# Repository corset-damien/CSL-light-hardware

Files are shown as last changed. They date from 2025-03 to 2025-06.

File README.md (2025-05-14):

# CSL-light-hardware

## I. Objectives 
### LED module operating modes with a pcb plate

#### MODE 1 - Sequence of pulses
The user can define on the computer the frequency and amplitude of a sequence of pulses.

#### MODE 2 - Analog control 
The user can send an analog signal to control the LED. The analog signal can be designed using eg. a signal generator. 

#### MODE 3 - Manual control
The user can set the LED level using a potentiometer.

## II. Usage

### I. Access mode 
- **To access Mode 1**: set interruptor to 1 ("serial" shows up on the screen) and switch the flip to PWM.
- **To access Mode 2**: set interruptor to 1 ("serial" shows up on the screen) and switch the flip to analog.
- **To access Mode 3**: set interruptor to 0 ("manual" shows up on the screen).

### II. Connection 
- Insert the LED jacks into the corresponding holes
- Insert the generator jacks into the corresponding holes
- Insert the jacks to feed the analog signals into the corresponding input holes

<p align="center">
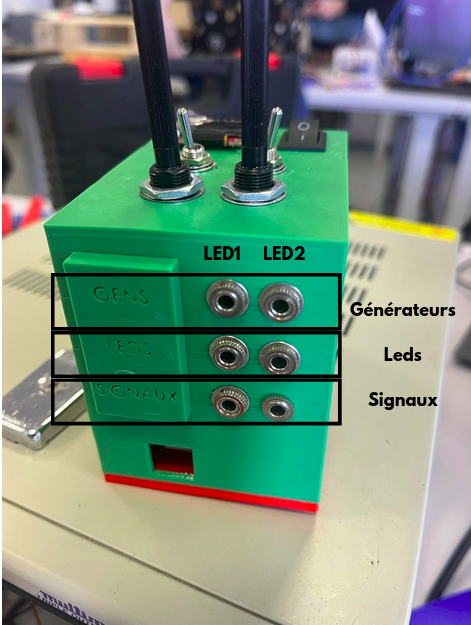
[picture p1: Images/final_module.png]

</p>

### III. Using the LEDControl_interrupt_screen_ascii code

First, open the LEDControl_interrupt_screen_ascii.cpp code in Arduino.ide.
To run the program, you must first have the SSD1306Ascii library installed on Arduino.

[Explains how to control light sources with Arduino and Python, and generate a trigger signal to synchronize a camera](https://github.com/SonyCSLParis/CSL-Lights)

Test the control command: 
- type: #d[3,0,0,1,0,2,0,255]:xxxx.  
  It is a command to generate on and off output on pin 3 or 6.
  The pin stays on for 1 seconds with a period of 2 seconds, at intensity 255. 
  It is later on embeded in a Pyton code for clarity. 
  You should see a character sequence appear. 
- Then type #b[100,0]:xxxx to start the experiment. 
  You should see the LEDs blink (frequency 0.5Hz). 
- To stop the blinking, type #e:xxxx

## III. Manufacture

### I. Kicad

[Kicad Folder](https://github.com/Julie-Mauguit/CSL-light-hardware/tree/main/Kicad%20pcb)

#### A. Complete electronic circuit

Complete Circuit on Kicad : 

<p align="center">
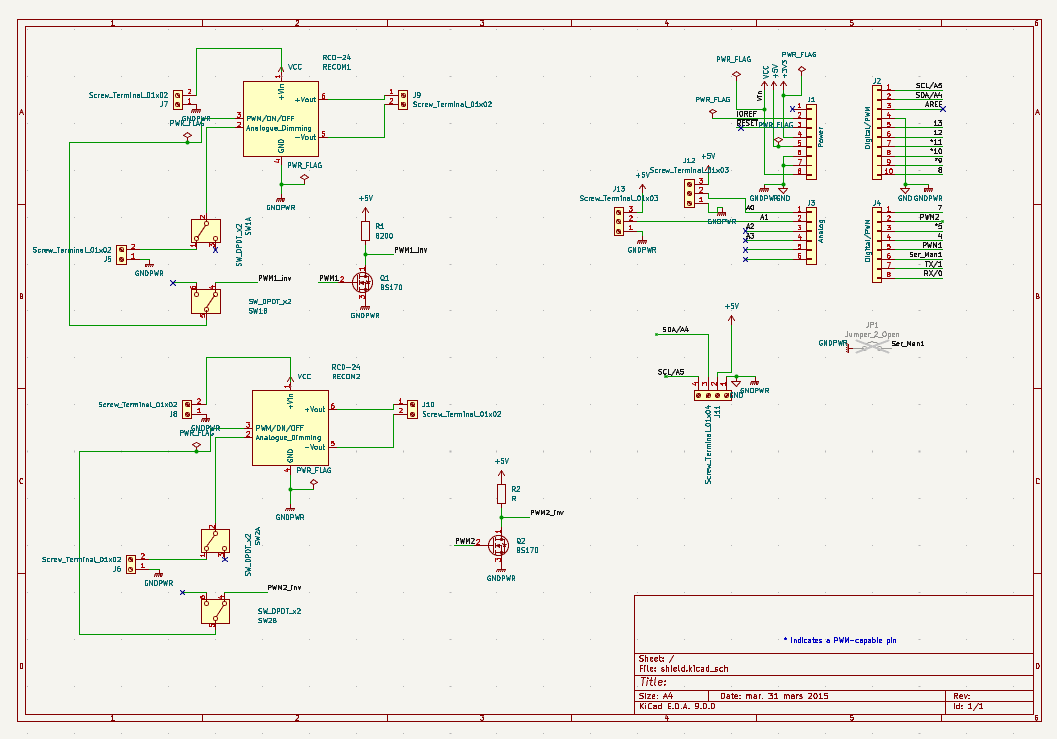
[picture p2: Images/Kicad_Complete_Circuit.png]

</p>

LED 1 and 2 : 

<p align="center">
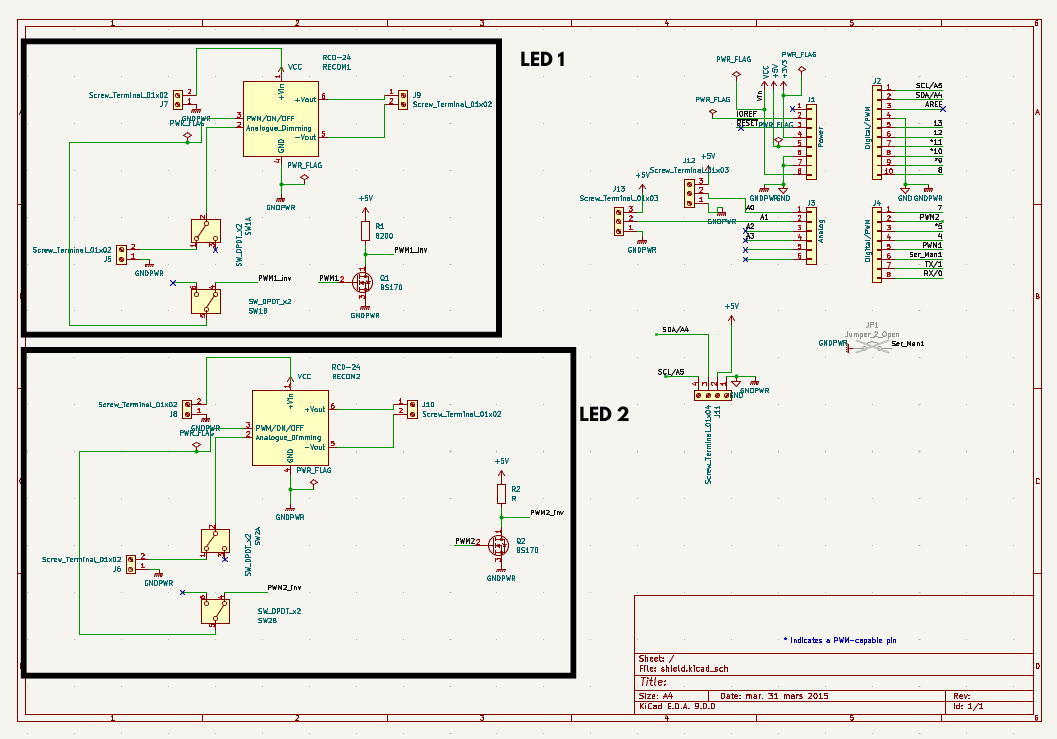
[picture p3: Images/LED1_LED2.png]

</p>

PWM Control : 

<p align="center">
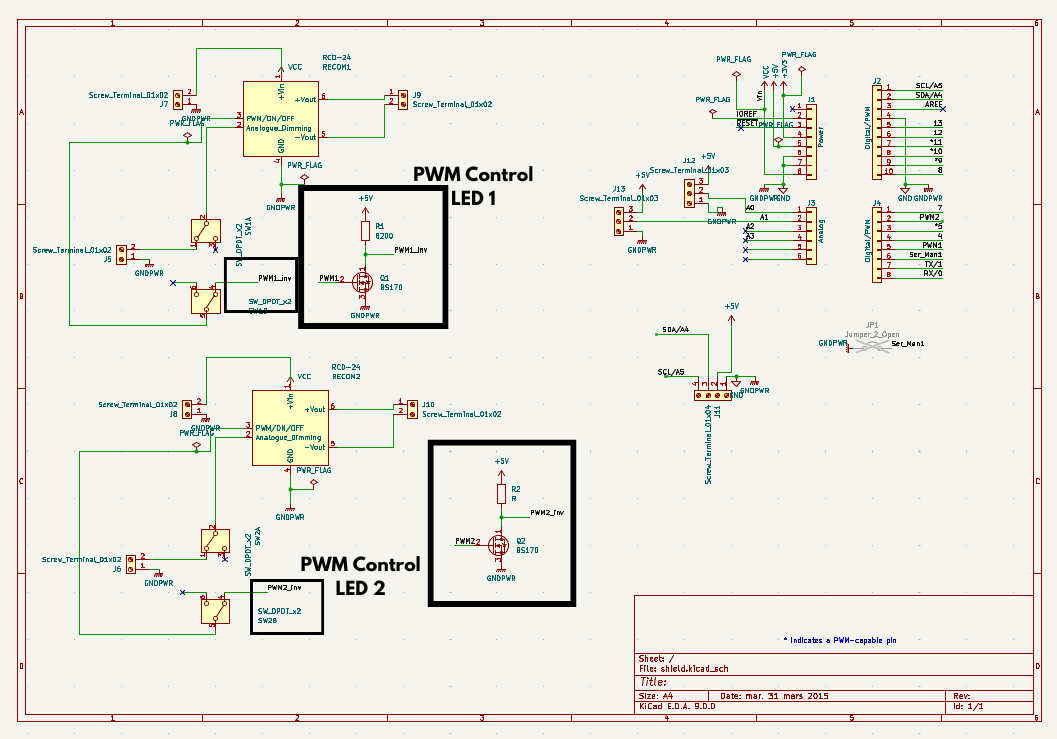
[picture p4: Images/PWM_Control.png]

</p>

Analog Control : 

<p align="center">
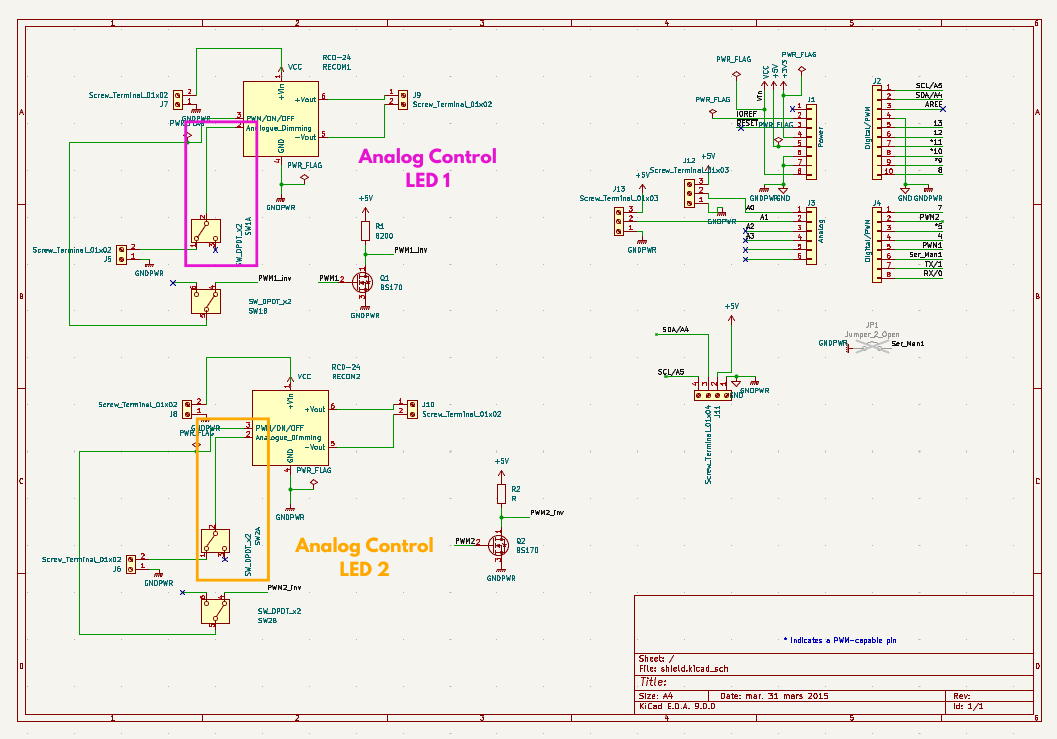
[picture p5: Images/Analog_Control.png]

</p>

Serial or Manual Mode : 

<p align="center">
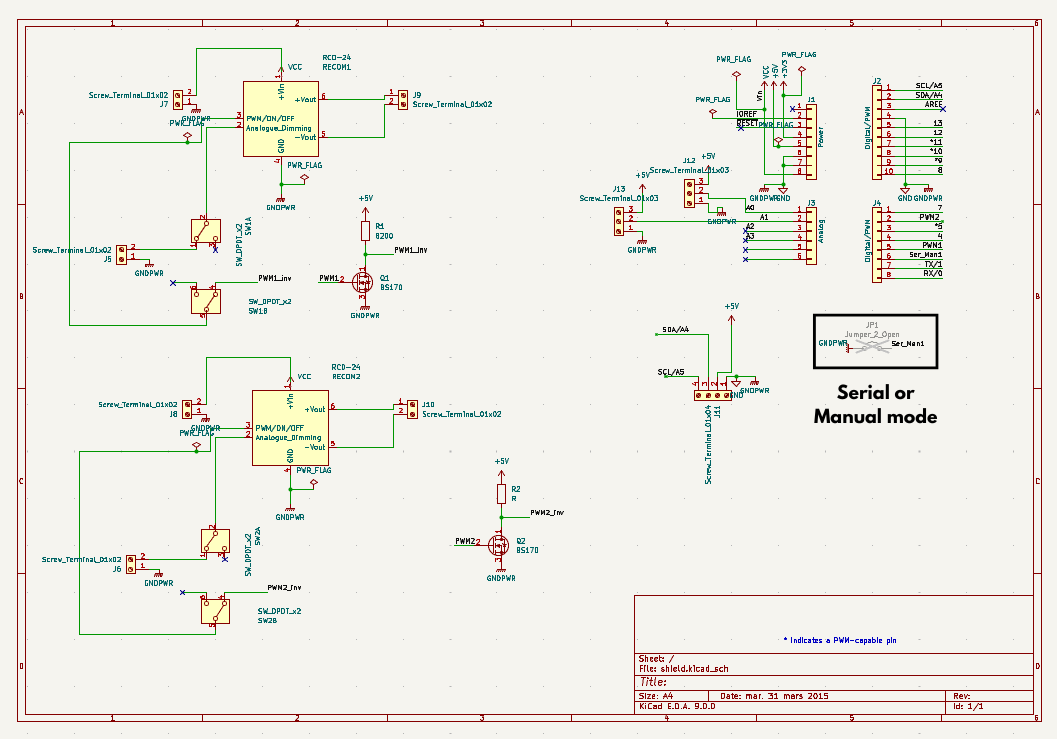
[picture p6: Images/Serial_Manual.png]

</p>

#### B. Component roles
- **Top connectors (J5, J7, J6, J8, J10)** :
  These are screw terminal blocks used to connect LEDs, power, or other peripherals.
- **Relays (RECOM1, RECOM2, etc.)** :
Their role is to adjust the LED light output to prevent damage. They therefore act as power regulators.
- **MOSFETs (BS170)** :
These are used to invert the signal. In fact, the RECOM inverts the input signal, it is inverted a first time before it processes it, in order to obtain the initially desired signal at the output. This can be useful if the LEDs require active low control (they light up when the signal is LOW).
- **Potentiometers (RV1, RV2)** :
These allow for a manual mode to adjust LED intensity via an analog input.
- **Double Switch (SW_DPDT_x2)** :
Two switches are used to select between analog or PWM control for each LED.
- **A Switch On-Off (Jumper_2_Open)** :
It allows switching between Serial and Manual modes.

#### C. Impression

It lasts about 30 minutes.

<p align="center">
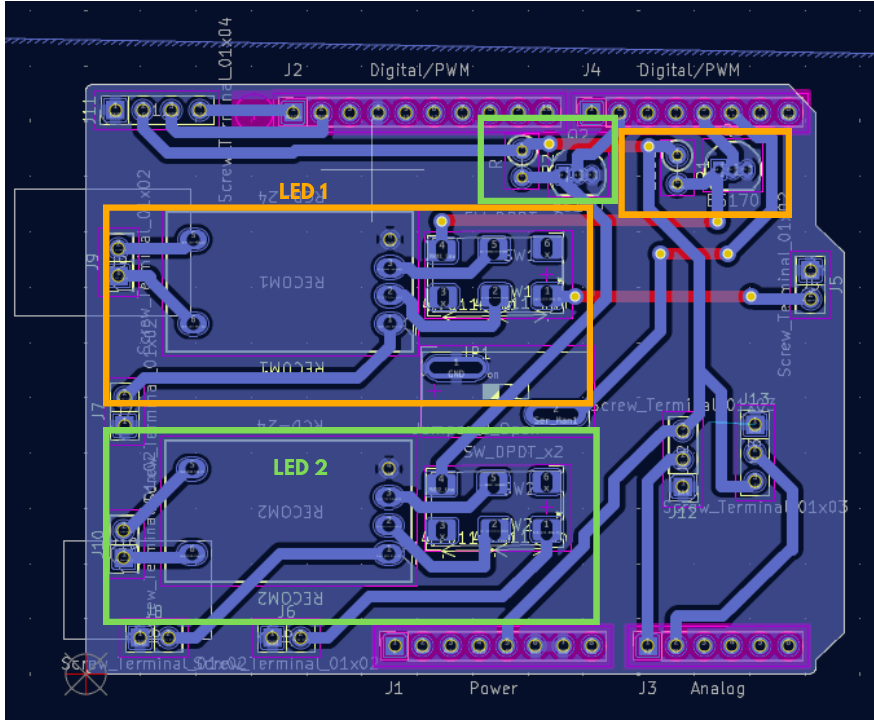
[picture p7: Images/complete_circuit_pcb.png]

</p>

### II. Welding

#### A. Shield Arduino
First, you need to solder the branches of the Arduino.

#### B. Components that you solder directly onto the PCB board
- Resistors
- MOSFET transistors
- RECOM
- Terminal blocks
- Vias

#### C. Components that you don't solder directly onto the PCB board
- The 2 potentiometers
- The OLED screen
- The 2 switches
- The on-off switch

<p align="center">
  <strong>After welding</strong><br>
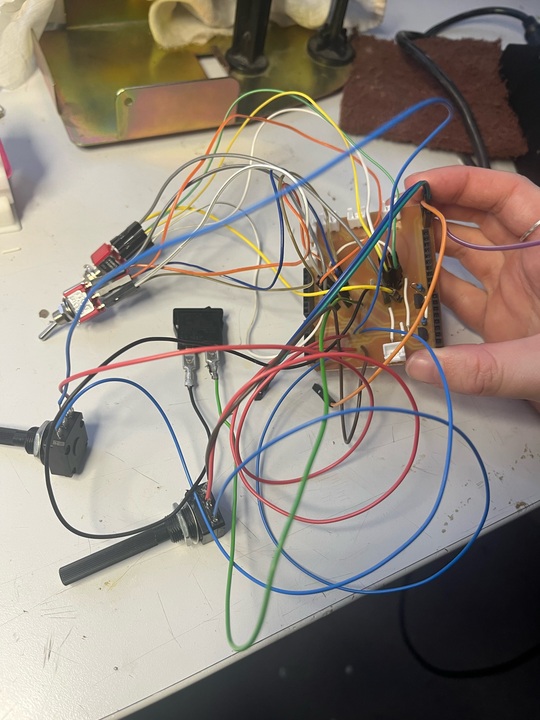
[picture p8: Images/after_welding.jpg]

</p>

#### D. Jack sockets
You have to solder cables with the female jack sockets.

<p align="center">
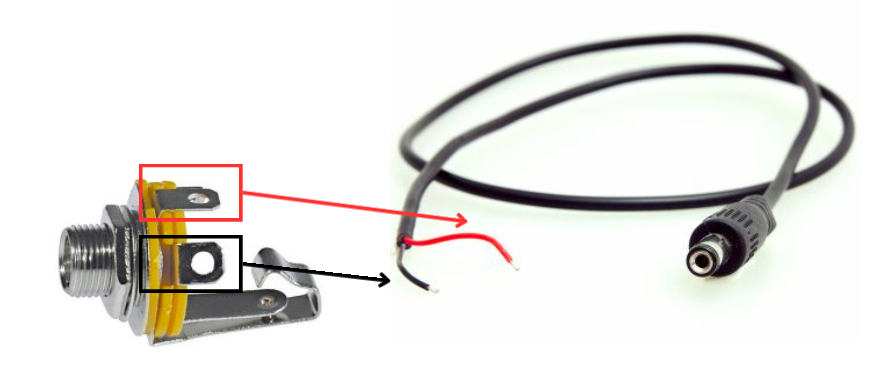
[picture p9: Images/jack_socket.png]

</p>

For the black and red cables of the male jack, you must solder them to the generator, LED, and signal cables.
Before soldering, prepare some heat-shrink tubing to prevent loose connections.

#### E. List of components

On GOTRRONIC : 

- **RECOM** : (x2)
  - Web link: https://www.gotronic.fr/art-convertisseur-r-78e3-3-0-5-29589.htm
  - Code : 14977
  - Price : 4,6€

- **Switch On-Off**: (x1)
  - Web link : https://www.gotronic.fr/art-inter-secteur-unipolaire-47432.htm
  - Code : 07059
  - Price : 0.90€

- **OLED Screen** : (x1)
  - Web link : https://www.gotronic.fr/art-module-afficheur-oled-0-96-tf052-28511.htm
  - Code : 36038
  - Price : 9,5€

- **Potentiometers** : (x2)
  - Web link : https://www.gotronic.fr/art-potentiometre-logarithmique-10k-937-3000.htm
  - Code : 04519
  - Price : 2,60€

 - **Double switch** : (x2)
    - Web link : https://www.gotronic.fr/art-inverseur-bipolaire-8012b-4181.htm
    - Code : 07014
    - Price : 2,80€
      
- **Resistors 820 ohms** : (x2)
    - Web link : https://www.gotronic.fr/art-resistance-carbone-1w-820-8486-2748.htm
    - Code :  04235
    - Price : 0,10€
      
- **2.5mm pitch terminal block** : (x6)
    - Web link : https://www.gotronic.fr/art-bornier-sc02-2-54-15468.htm
    - Code : 48930
    - Price : 0.80€
      
 - **3.5 mm male jack** : (x6)
    - Web link : https://www.gotronic.fr/art-cordon-jack-vers-fils-denudes-sterf-37803.htm
    - Code : 48239
    - Price : 0,95€
  
 - **3.5mm female socket** : (x6)
     - Web link : https://www.gotronic.fr/art-embase-femelle-cg203-4814.htm
     - Code : 08461
     - Price : 0,50€

 - **Transistor MOSFET BS170** : (x2)
     - Web link : https://www.gotronic.fr/art-transistor-bs170-1569.htm
     - Code : 02440
     - Price : 0.30€

- **Uno Arduino** : (x1)
    - Web link : https://www.gotronic.fr/art-arduino-uno-a000066-12420.htm
    - Code : 25950
    - Price : 23.90€

- **9-pin Arduino connector** : (x3)
    - Web link : https://www.gotronic.fr/art-connecteur-fh1x9-35491.htm
    - Code : 49007
    - Price : 0.80€
      
- **14-pin Arduino connector** : (x1)
    - Web link : https://www.gotronic.fr/art-connecteur-fh1x14-35646.htm
    - Code : 49011
    - Price : 1€
      
- **LED** : (x2)
    - Web link: https://www.gotronic.fr/art-led-5-mm-led5bt-21009.htm
    - Code :  03039
    - Price : 0.30€

### III. Assembly

#### A. Box printing

[Solidworks box](https://github.com/Julie-Mauguit/CSL-light-hardware/tree/main/Solidworks%20bo%C3%AEte)

Printing the box takes approximately 1 hour and 20 minutes.
Printing the box lid takes approximately 30 minutes.
Printing the small panel with the instructions takes approximately 13 minutes.

#### B. Plastic inserts

You will need to make three 3.7mm diameter, 3mm deep plastic inserts with 6mm long M3 screws to secure the Arduino to the enclosure lid. 
Then, make 3mm diameter, 3mm deep plastic inserts with 8mm long M3 screws to close the enclosure.

#### C. Finalization

Screw the components into the box in this order:
- Female jack sockets
- OLED display with 10mm long M2 screws and nuts
- The two switches
- The on-off switch
- The two potentiometers

<p align="center">
  <strong>After assembly</strong><br>
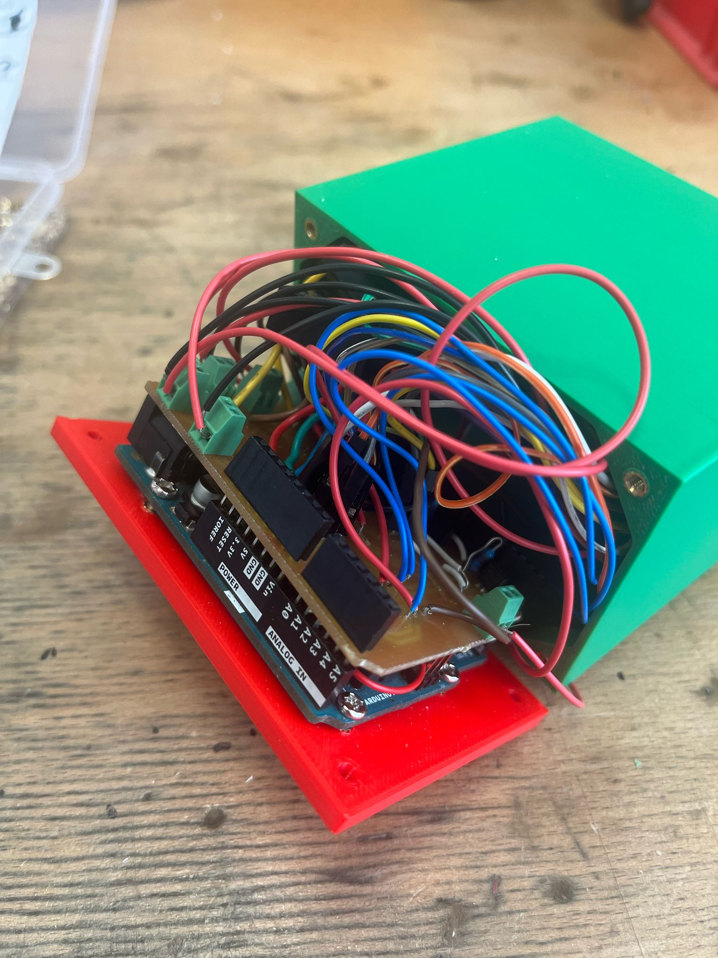
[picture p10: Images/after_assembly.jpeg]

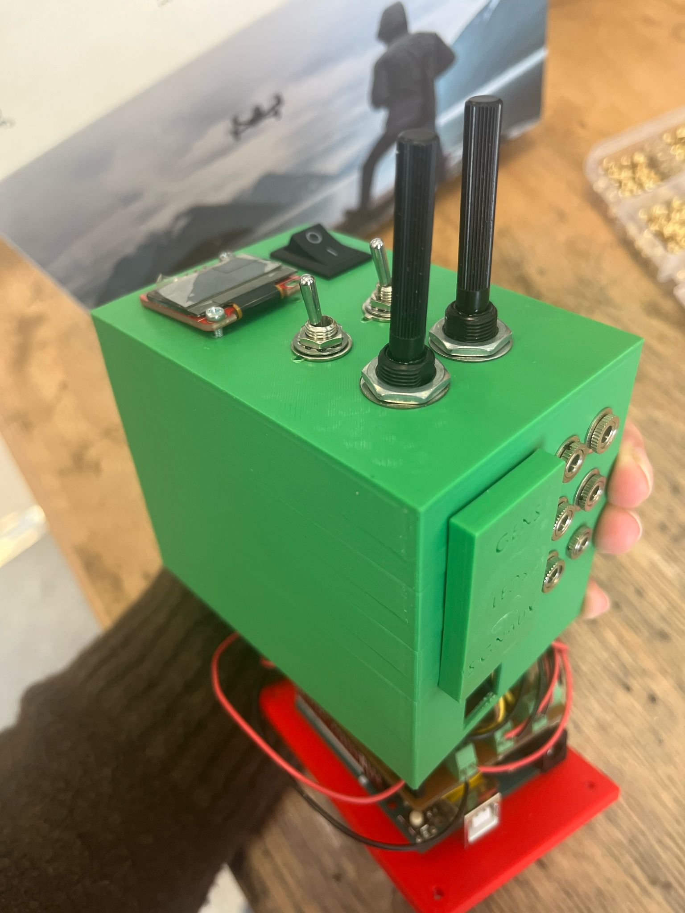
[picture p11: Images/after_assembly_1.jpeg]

</p>

### IV. Code

[Code Arduino/LEDControl_interrupt_screen_ascii](https://github.com/Julie-Mauguit/CSL-light-hardware/tree/main/Code%20Arduino/LEDControl_interrupt_screen_ascii)

The code has been adapted to suit the circuit. 
In this configuration, pins 3 and 6 are used for PWM inputs, while pins A0 and A1 are used for analog inputs.

[Explains how to control light sources with Arduino and Python, and generate a trigger signal to synchronize a camera](https://github.com/SonyCSLParis/CSL-Lights)

### License

Copyright (C) 2025 

Author(s):
Julie Maugit - Polytech Sorbonne
Thierry Legou - CNRS/Aix-Marseille Université
Peter Hanappe - Sony Computer Science Laboratories Paris
Aliénor Lahlou - Sony Computer Science Laboratories Paris

You can redistribute it and/or modify  it under the terms of the GNU General Public License as published by   the Free Software Foundation, either version 3 of the License, or   (at your option) any later version.  This project is distributed in the hope that it will be useful, but  WITHOUT ANY WARRANTY; without even the implied warranty of   MERCHANTABILITY or FITNESS FOR A PARTICULAR PURPOSE.  See the GNU  General Public License for more details.  You should have received a copy of the GNU General Public License  along with this program.  If not, see  <http://www.gnu.org/licenses/>.

This work was supported by the European Innovation Council Pathfinder Open DREAM (grant no. 101046451)

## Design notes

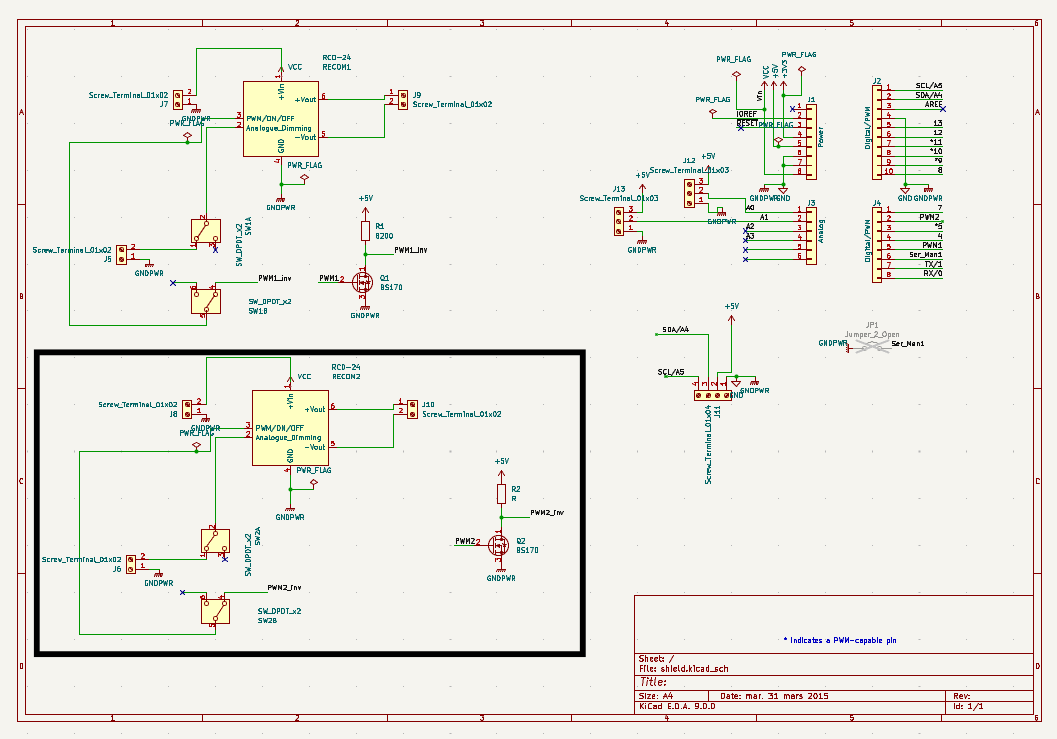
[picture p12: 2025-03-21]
Images/LED 2.png

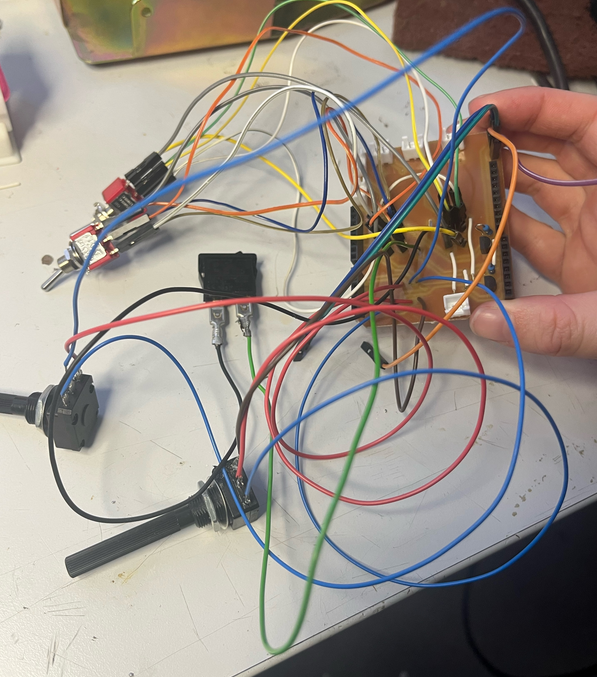
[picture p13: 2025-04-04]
Images/pcb_plate.png

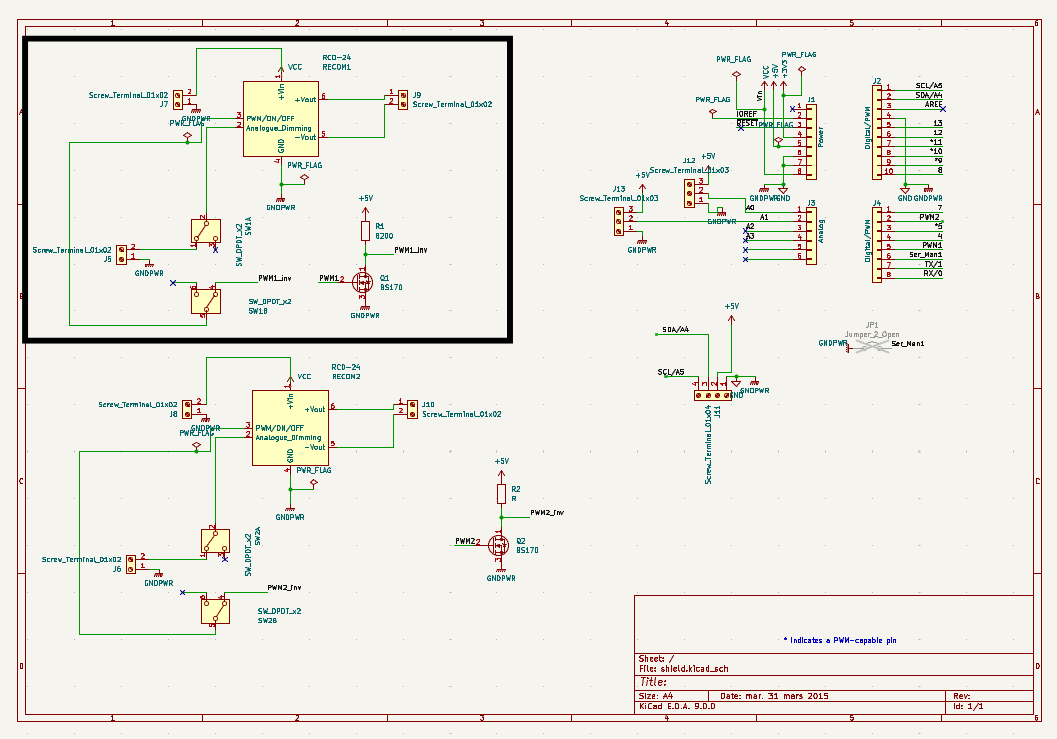
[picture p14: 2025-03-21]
Images/LED 1.png

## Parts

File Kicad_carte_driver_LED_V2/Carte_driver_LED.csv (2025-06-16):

Source: | C:\Users\damie\OneDrive\Bureau\Stage_Sony_CSL_CORSET_Damien\Projets_principaux\led_controler\Kicad\Carte_driver_LED\Carte_driver_LED.kicad_sch
Date: | 28/04/2025 18:29:50
Tool: | Eeschema 7.0.10
Generator: | C:\Program Files\KiCad\7.0\bin\scripting\plugins/bom_csv_grouped_by_value.py
Component Count: | 41
Collated Components:
Item | Qty | Reference(s) | Value | LibPart | Footprint | Datasheet | DNP | Availability | Check_prices | Description | MANUFACTURER | MF | MP | PARTREV | Package | Price | STANDARD | SnapEDA_Link
1 | 2 | C1, C2 | 2.2u | Device:C | Capacitor_SMD:CP_Elec_5x5.3 | ~
2 | 2 | C3, C4 | 10n | Device:C | Capacitor_SMD:C_1206_3216Metric_Pad1.33x1.80mm_HandSolder | ~
3 | 4 | C5, C6, C9, C10 | 2.2n | Device:C | Capacitor_SMD:C_1206_3216Metric_Pad1.33x1.80mm_HandSolder | ~
4 | 8 | C7, C8, C11, C12, C13, C14, C15, C16 | 100n | Device:C | Capacitor_SMD:C_1206_3216Metric_Pad1.33x1.80mm_HandSolder | ~
5 | 2 | C17, C20 | 10u | Device:C | Capacitor_SMD:CP_Elec_5x5.3 | ~
6 | 1 | C18 | 100n | Device:C | Capacitor_Tantalum_SMD:CP_EIA-1608-08_AVX-J_Pad1.25x1.05mm_HandSolder | ~
7 | 1 | C19 | 100n | Device:C | Capacitor_SMD:CP_Elec_5x5.3 | ~
8 | 1 | D1 | D_Schottky | Device:D_Schottky | Diode_SMD:D_1206_3216Metric_Pad1.42x1.75mm_HandSolder | ~
9 | 4 | H1, H2, H3, H4 | MountingHole | Mechanical:MountingHole | MountingHole:MountingHole_3.2mm_M3 | ~
10 | 1 | J1 | XT30 | XT30:Conn_01x02 | Connector_AMASS:AMASS_XT30U-F_1x02_P5.0mm_Vertical | ~
11 | 1 | J3 | EcranIHM | Connector_Generic:Conn_01x04 | Connector_PinHeader_2.54mm:PinHeader_1x04_P2.54mm_Vertical | ~
12 | 1 | J4 | XT30_OUT1 | XT30:Conn_01x02 | Connector_AMASS:AMASS_XT30U-F_1x02_P5.0mm_Vertical | ~
13 | 1 | J5 | XT30_OUT2 | XT30:Conn_01x02 | Connector_AMASS:AMASS_XT30U-F_1x02_P5.0mm_Vertical | ~
14 | 1 | J6 | AN2 | Connector_Generic:Conn_01x01 |  | ~
15 | 1 | J7 | Signal1 | Connector:Conn_Coaxial |  | ~
16 | 1 | J8 | Signal2 | Connector:Conn_Coaxial |  | ~
17 | 1 | J9 | Encodeur Rotatif | Connector_Generic:Conn_01x03 |  | ~
18 | 1 | J10 | Trigger | Connector_Generic:Conn_01x01 |  | ~
19 | 1 | J11 | AN1 | Connector_Generic:Conn_01x01 |  | ~
20 | 2 | L1, L2 | 220u | Device:L | Inductor_SMD:L_1206_3216Metric_Pad1.42x1.75mm_HandSolder | ~
21 | 1 | U1 | TSR1-2450E | Regulator_Switching:TSR1-2450E | Converter_DCDC:Converter_DCDC_TRACO_TSR1-xxxxE_THT | https://www.tracopower.com/products/tsr1e.pdf
22 | 1 | U2 | ESP32-DEVKITC | ESP32-DEVKITC:ESP32-DEVKITC | ESP32-DEVKITC:MODULE_ESP32-DEVKITC |  |  | In Stock | https://www.snapeda.com/parts/ESP32-DEVKITC/Olimex+LTD/view-part/?ref=eda | - ESP32-WROOM32 Transceiver; 802.11 b/g/n (Wi-Fi, WiFi, WLAN), Bluetooth® Smart 4.x Low Energy (BLE) 2.4GHz Evaluation Board | ESPRESSIF | Olimex LTD | ESP32-DEVKITC | N/A | None | None | Manufacturer Recommendations | https://www.snapeda.com/parts/ESP32-DEVKITC/Olimex+LTD/view-part/?ref=snap
23 | 1 | U3 | RCD-24_1 | RCD-24:RCD-24_1 | Converter_DCDC:Converter_DCDC_RECOM_RCD-24_THT
24 | 1 | U4 | RCD-24_2 | :RCD-24_1_1 | Converter_DCDC:Converter_DCDC_RECOM_RCD-24_THT

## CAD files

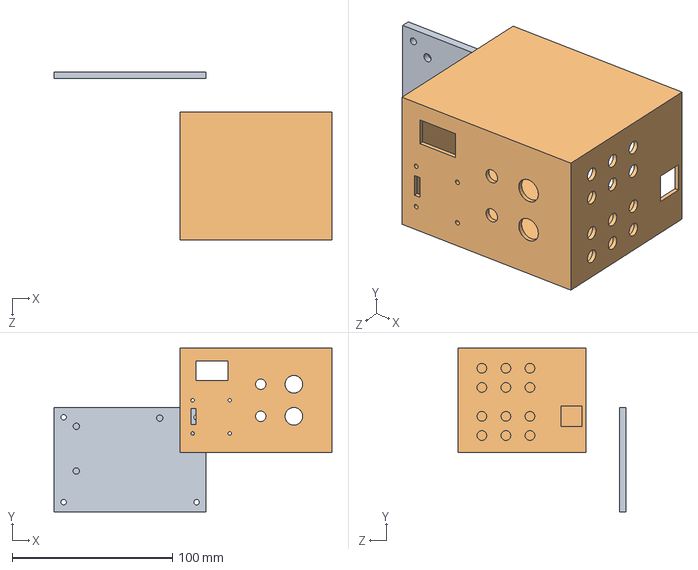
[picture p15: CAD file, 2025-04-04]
Solidworks boîte/Assemblage1.SLDASM
173.5 x 102.1 x 105.0 mm
boîte_pcb
couvercle_pcb

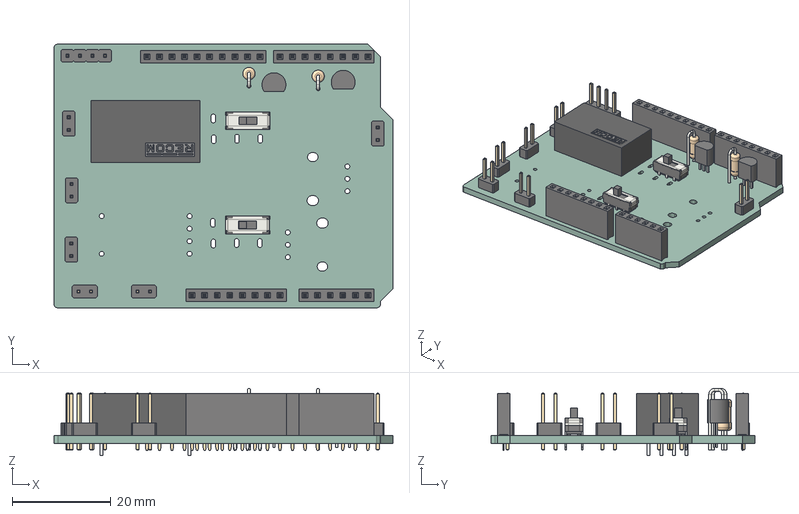
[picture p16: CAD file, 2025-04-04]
Kicad pcb/shield.step
68.6 x 53.3 x 13.6 mm
PinSocket_1x08_P2.54mm_Vertical x 2
PinSocket_1x06_P2.54mm_Vertical
PinSocket_1x10_P2.54mm_Vertical
PinHeader_2x01_P254mm_Vertical x 6
RCD-24_case
RCD-24_pin6(+Vout)
RCD-24_potting
RCD-24_pin2(Analogue_dimming)
RCD-24_pin1(+Vin)
RCD-24_pin3(PWM_ON_OFF_or_Vref)
RCD-24_pin4(GND)
RCD-24_pin5(-Vout)
CuK_JS202011CQN_DPDT_straight x 2
R_Axial_DIN0207_L63mm_D25mm_P254mm_Vertical x 2
PinHeader_1x04_P254mm_Vertical
TO-92_Inline_Narrow x 2
shield_PCB

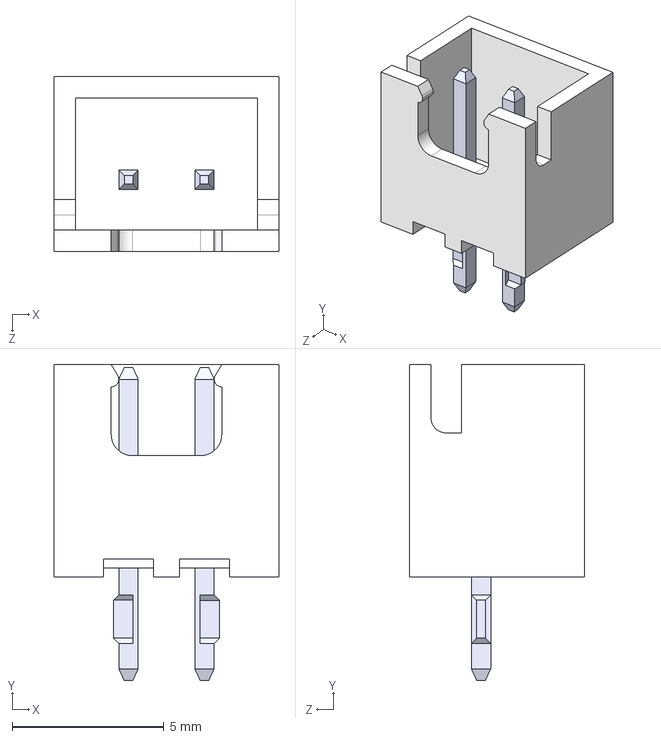
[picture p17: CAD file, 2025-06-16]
Kicad_carte_driver_LED_V2/Lib_carte_driver_LED/3D/JST_2.50mm/B2B-XH-A.step
7.40 x 10.4 x 5.75 mm

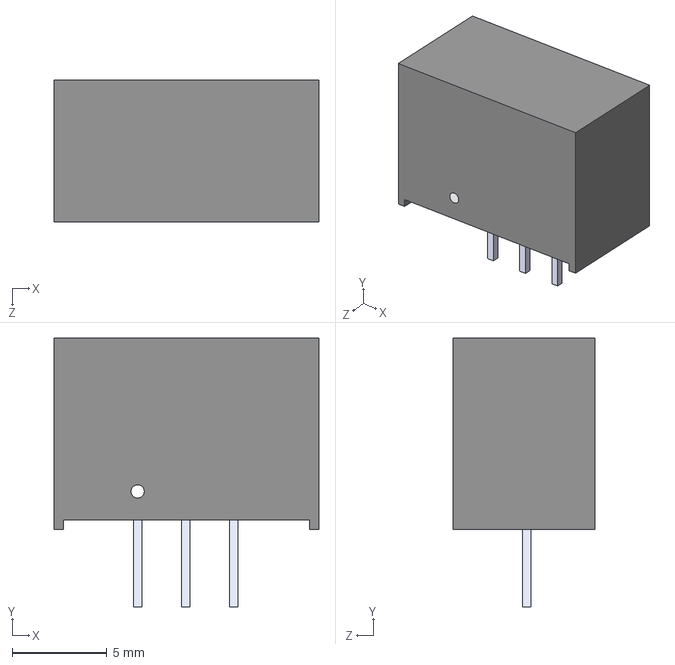
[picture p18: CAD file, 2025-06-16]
Kicad_carte_driver_LED_V2/Lib_carte_driver_LED/3D/TSR_2-2450.step
14.0 x 14.2 x 7.50 mm

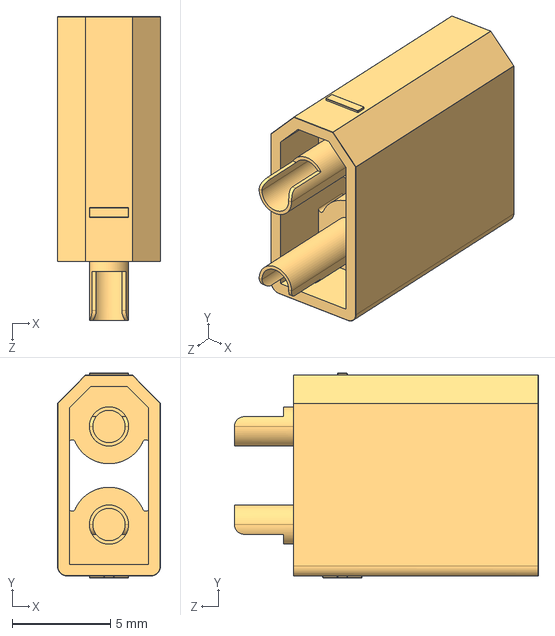
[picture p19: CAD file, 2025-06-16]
Kicad_carte_driver_LED_V2/Lib_carte_driver_LED/3D/XT_30_M/XT30U-M.step
5.25 x 10.4 x 15.5 mm

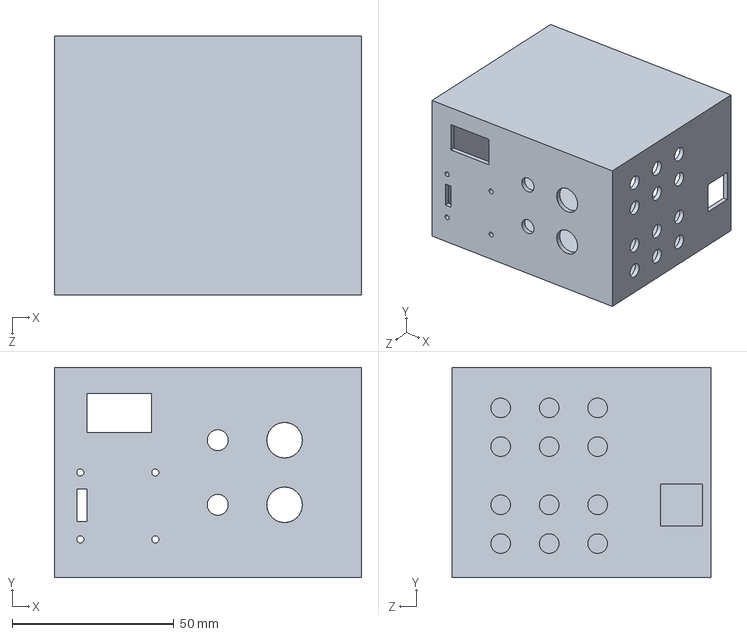
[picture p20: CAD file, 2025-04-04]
Solidworks boîte/boîte_pcb.SLDPRT
95.0 x 65.0 x 80.0 mm

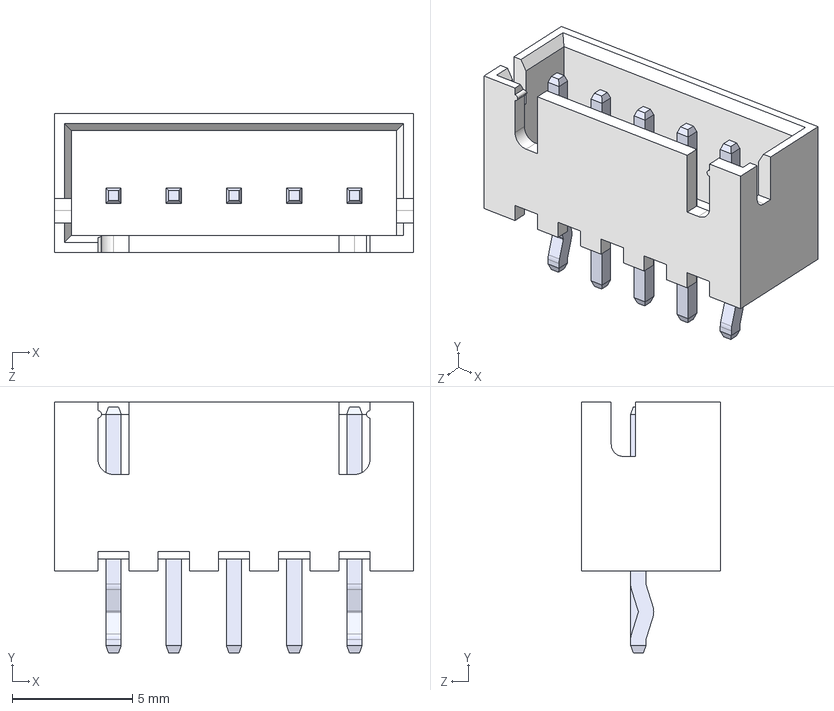
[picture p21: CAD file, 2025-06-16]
Kicad_carte_driver_LED_V2/Lib_carte_driver_LED/3D/JST_2.50mm/B5B-XH-A.step
14.9 x 10.4 x 5.75 mm

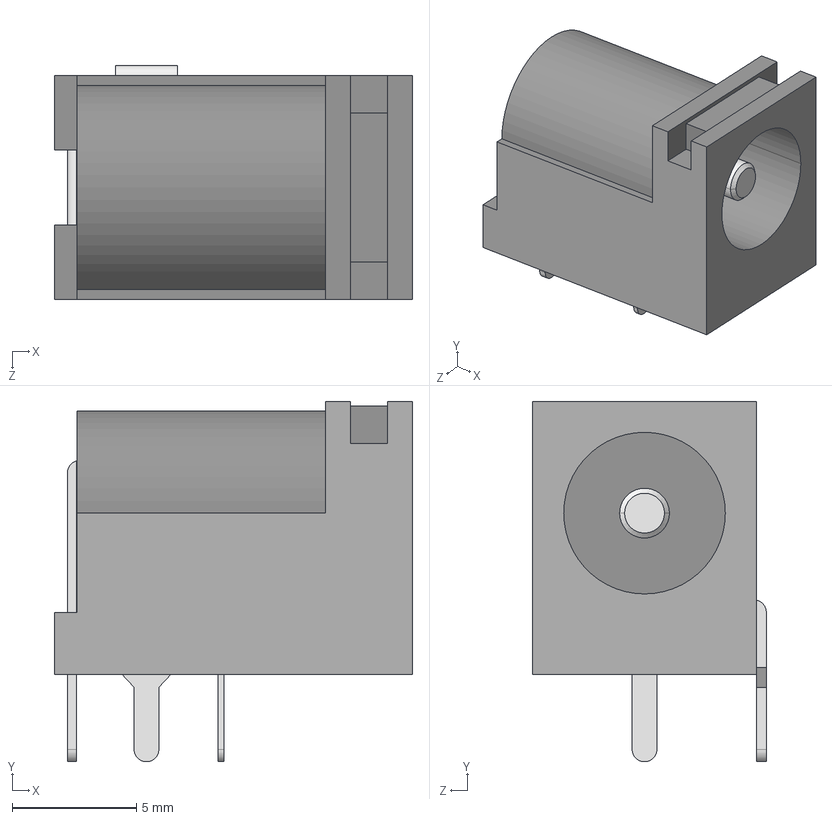
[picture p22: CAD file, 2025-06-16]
Kicad_carte_driver_LED_V2/Lib_carte_driver_LED/3D/PJ-102AH.step
14.4 x 14.5 x 9.40 mm

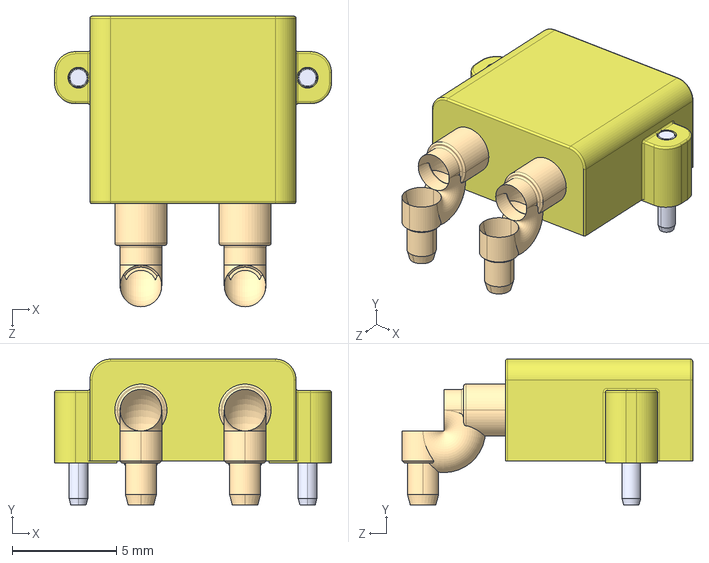
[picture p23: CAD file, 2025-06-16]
Kicad_carte_driver_LED_V2/Lib_carte_driver_LED/3D/XT_30_M/XT30PW-M.step
13.3 x 7.00 x 14.0 mm

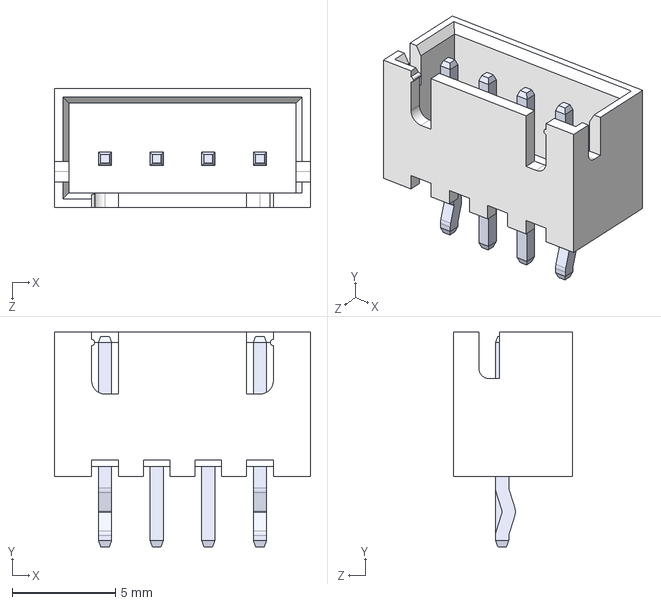
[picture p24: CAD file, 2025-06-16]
Kicad_carte_driver_LED_V2/Lib_carte_driver_LED/3D/JST_2.50mm/B4B-XH-A.step
12.4 x 10.4 x 5.75 mm

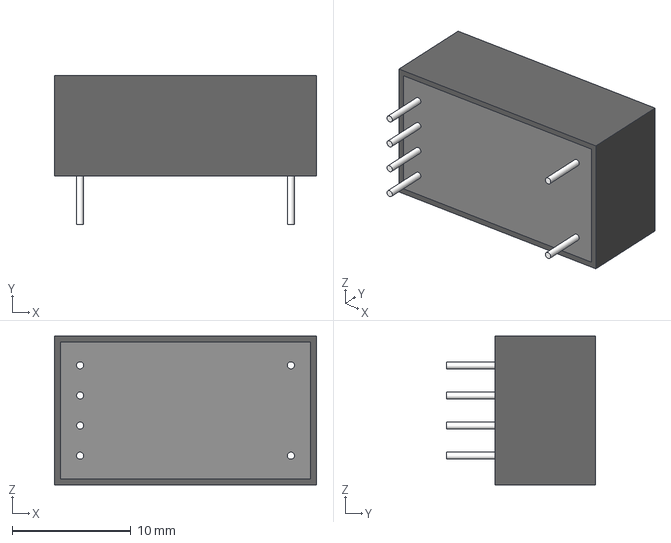
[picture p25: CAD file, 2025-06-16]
Kicad_carte_driver_LED_V2/Lib_carte_driver_LED/3D/RCD-24-1.20.step
22.1 x 12.6 x 12.6 mm

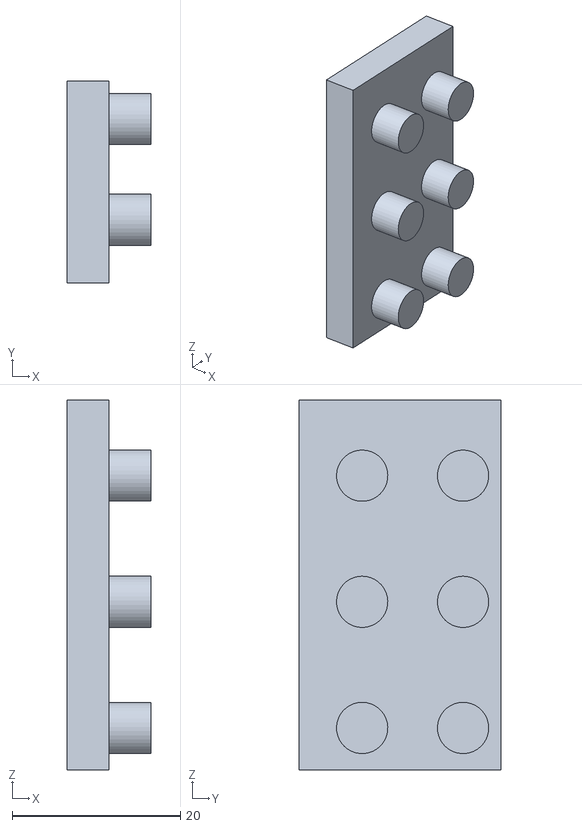
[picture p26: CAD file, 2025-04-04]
Solidworks boîte/petit_panneau.STL
10.0 x 24.0 x 44.0

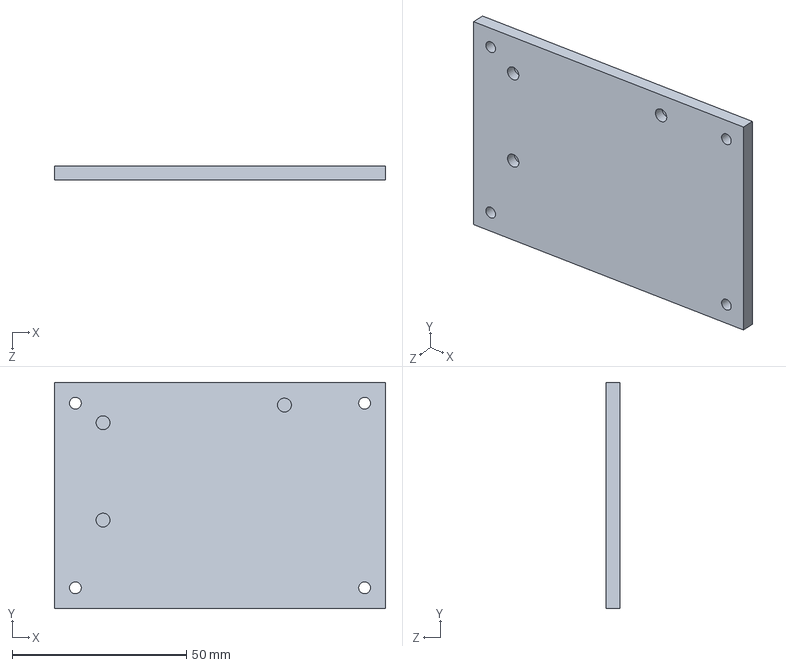
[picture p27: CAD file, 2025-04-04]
Solidworks boîte/couvercle_pcb.SLDPRT
95.0 x 65.0 x 4.00 mm

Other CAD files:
Kicad_carte_driver_LED_V2/Lib_carte_driver_LED/3D/JST_2.50mm/S6B-XH-A.step
Solidworks boîte/boîte_pcb.STL
Solidworks boîte/couvercle_pcb.STL

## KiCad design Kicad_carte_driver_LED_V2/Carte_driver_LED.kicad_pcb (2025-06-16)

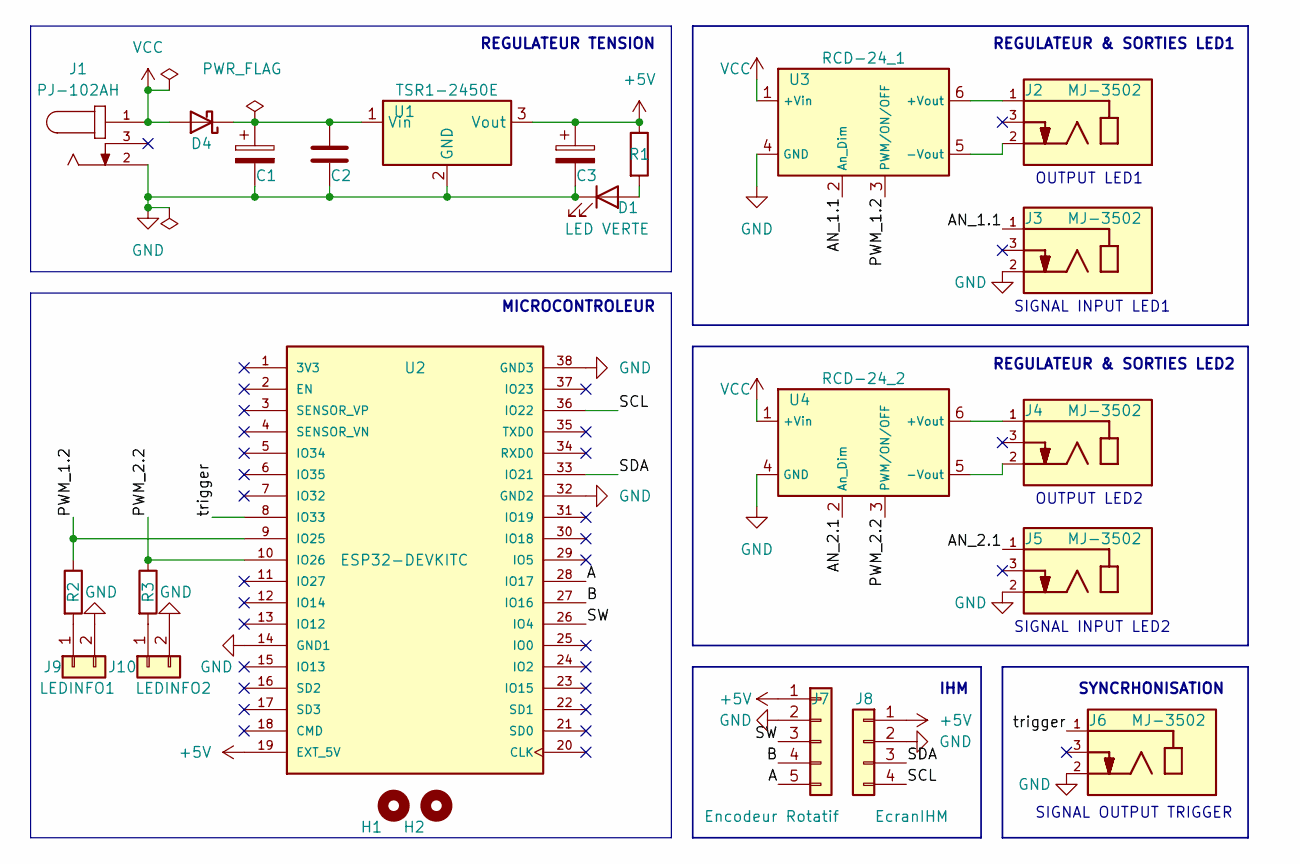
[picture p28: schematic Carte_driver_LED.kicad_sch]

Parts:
C1: 10u; CP_Axial_L10.0mm_D6.0mm_P15.00mm_Horizontal
C2: 100n; C_Rect_L7.0mm_W2.5mm_P5.00mm
C3: 100u; CP_Axial_L10.0mm_D6.0mm_P15.00mm_Horizontal
D1: LED VERTE; LED_D3.0mm
D4: D_Schottky; D_DO-41_SOD81_P10.16mm_Horizontal
H1, H2: MountingHole; MountingHole_3.2mm_M3
J1: PJ-102AH; CUI_PJ-102AH
J2, J3, J4, J5, J6: MJ-3502; CUI_MJ-3502; PART_REV A
J7: Encodeur Rotatif; JST_XH_B5B-XH-A_1x05_P2.50mm_Vertical
J8: EcranIHM; JST_XH_B4B-XH-A_1x04_P2.50mm_Vertical
J9: LEDINFO1; JST_XH_B2B-XH-A_1x02_P2.50mm_Vertical
J10: LEDINFO2; JST_XH_B2B-XH-A_1x02_P2.50mm_Vertical
R1: R; R_Axial_DIN0207_L6.3mm_D2.5mm_P7.62mm_Horizontal
R2, R3: R; R_Axial_DIN0207_L6.3mm_D2.5mm_P10.16mm_Horizontal
U1: TSR1-2450E; TSR_2-2450
U2: ESP32-DEVKITC; MODULE_ESP32-DEVKITC; PARTREV N/A
U3: RCD-24_1; CONV_RCD-24-1.20
U4: RCD-24_2; CONV_RCD-24-1.20

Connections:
+5V: C3.1, J7.1, J8.1, R1.1, U1.3 (Vout), U2.19 (EXT_5V)
/A: J7.5, U2.28 (IO17)
/AN_1.1: J3.1, U3.2 (An_Dim)
/AN_2.1: J5.1, U4.2 (An_Dim)
/B: J7.4, U2.27 (IO16)
/PWM_1.2: R2.1, U2.9 (IO25), U3.3 (PWM/ON/OFF)
/PWM_2.2: R3.1, U2.10 (IO26), U4.3 (PWM/ON/OFF)
/SCL: J8.4, U2.36 (IO22)
/SDA: J8.3, U2.33 (IO21)
/SW: J7.3, U2.26 (IO4)
/trigger: J6.1, U2.8 (IO33)
GND: C1.2, C2.2, C3.2, D1.1 (K), J1.2, J3.2, J5.2, J6.2, J7.2, J8.2, J9.2, J10.2, U1.2 (GND), U2.14 (GND1), U2.32 (GND2), U2.38 (GND3), U3.4 (GND), U4.4 (GND)
unnamed: D1.2 (A), R1.2
unnamed: C1.1, C2.1, D4.1 (K), U1.1 (Vin)
unnamed: J9.1, R2.2
unnamed: J10.1, R3.2
unnamed: J2.1, U3.6 (+Vout)
unnamed: J2.2, U3.5 (-Vout)
unnamed: J4.1, U4.6 (+Vout)
unnamed: J4.2, U4.5 (-Vout)
VCC: D4.2 (A), J1.1, U3.1 (+Vin), U4.1 (+Vin)

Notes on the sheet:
SIGNAL INPUT LED1
OUTPUT LED2
SIGNAL OUTPUT TRIGGER
SIGNAL INPUT LED2
REGULATEUR TENSION
MICROCONTROLEUR
SYNCRHONISATION
OUTPUT LED1
IHM
REGULATEUR & SORTIES LED2
REGULATEUR & SORTIES LED1

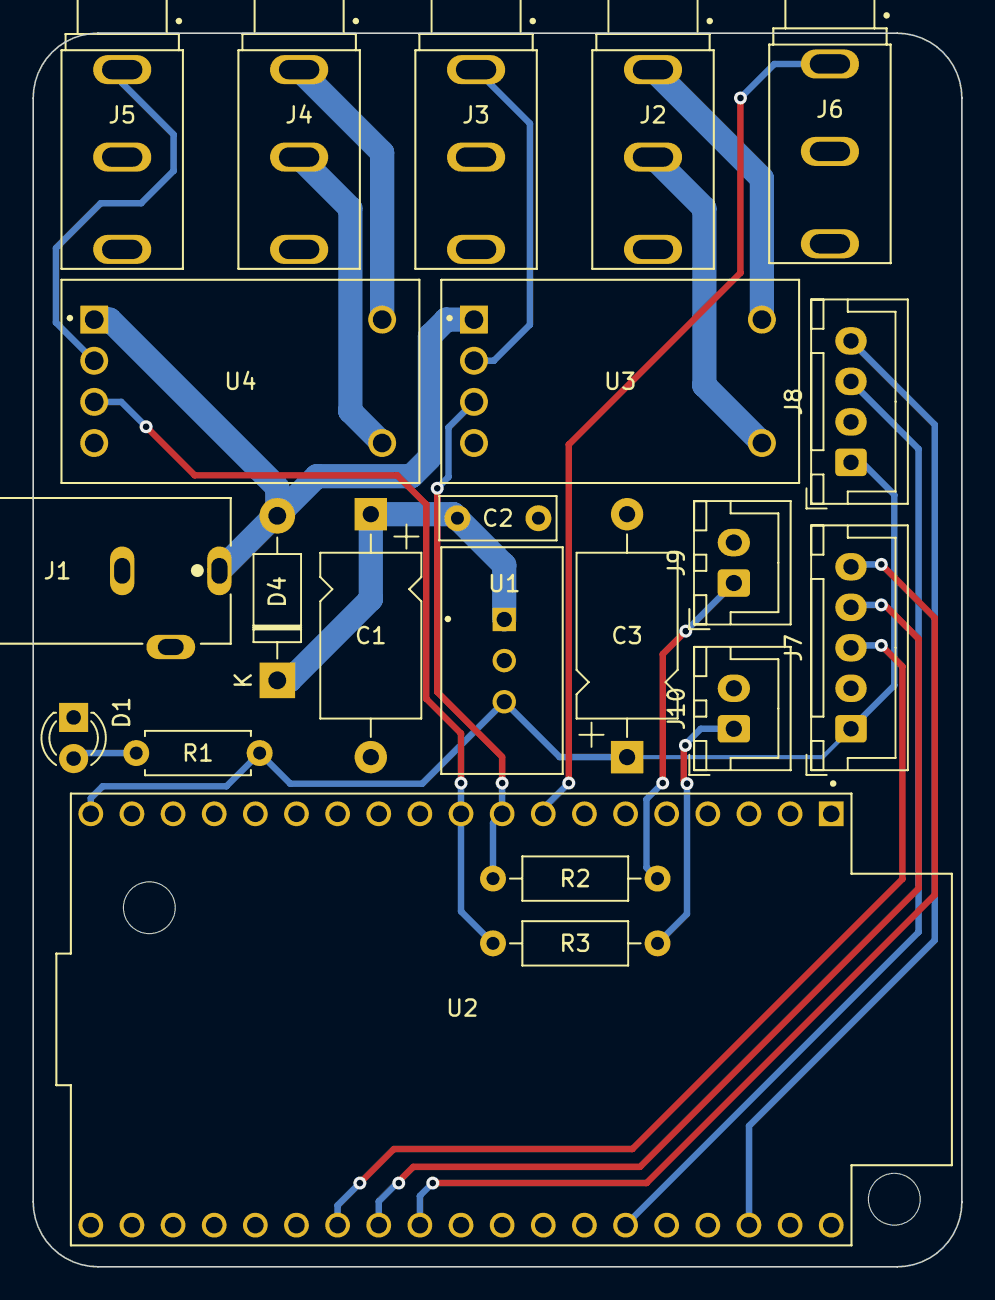
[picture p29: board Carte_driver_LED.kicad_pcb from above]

Board: 2 copper layers, 57.3 x 76.2 mm, 24 parts (0 on the bottom side), 21 nets.

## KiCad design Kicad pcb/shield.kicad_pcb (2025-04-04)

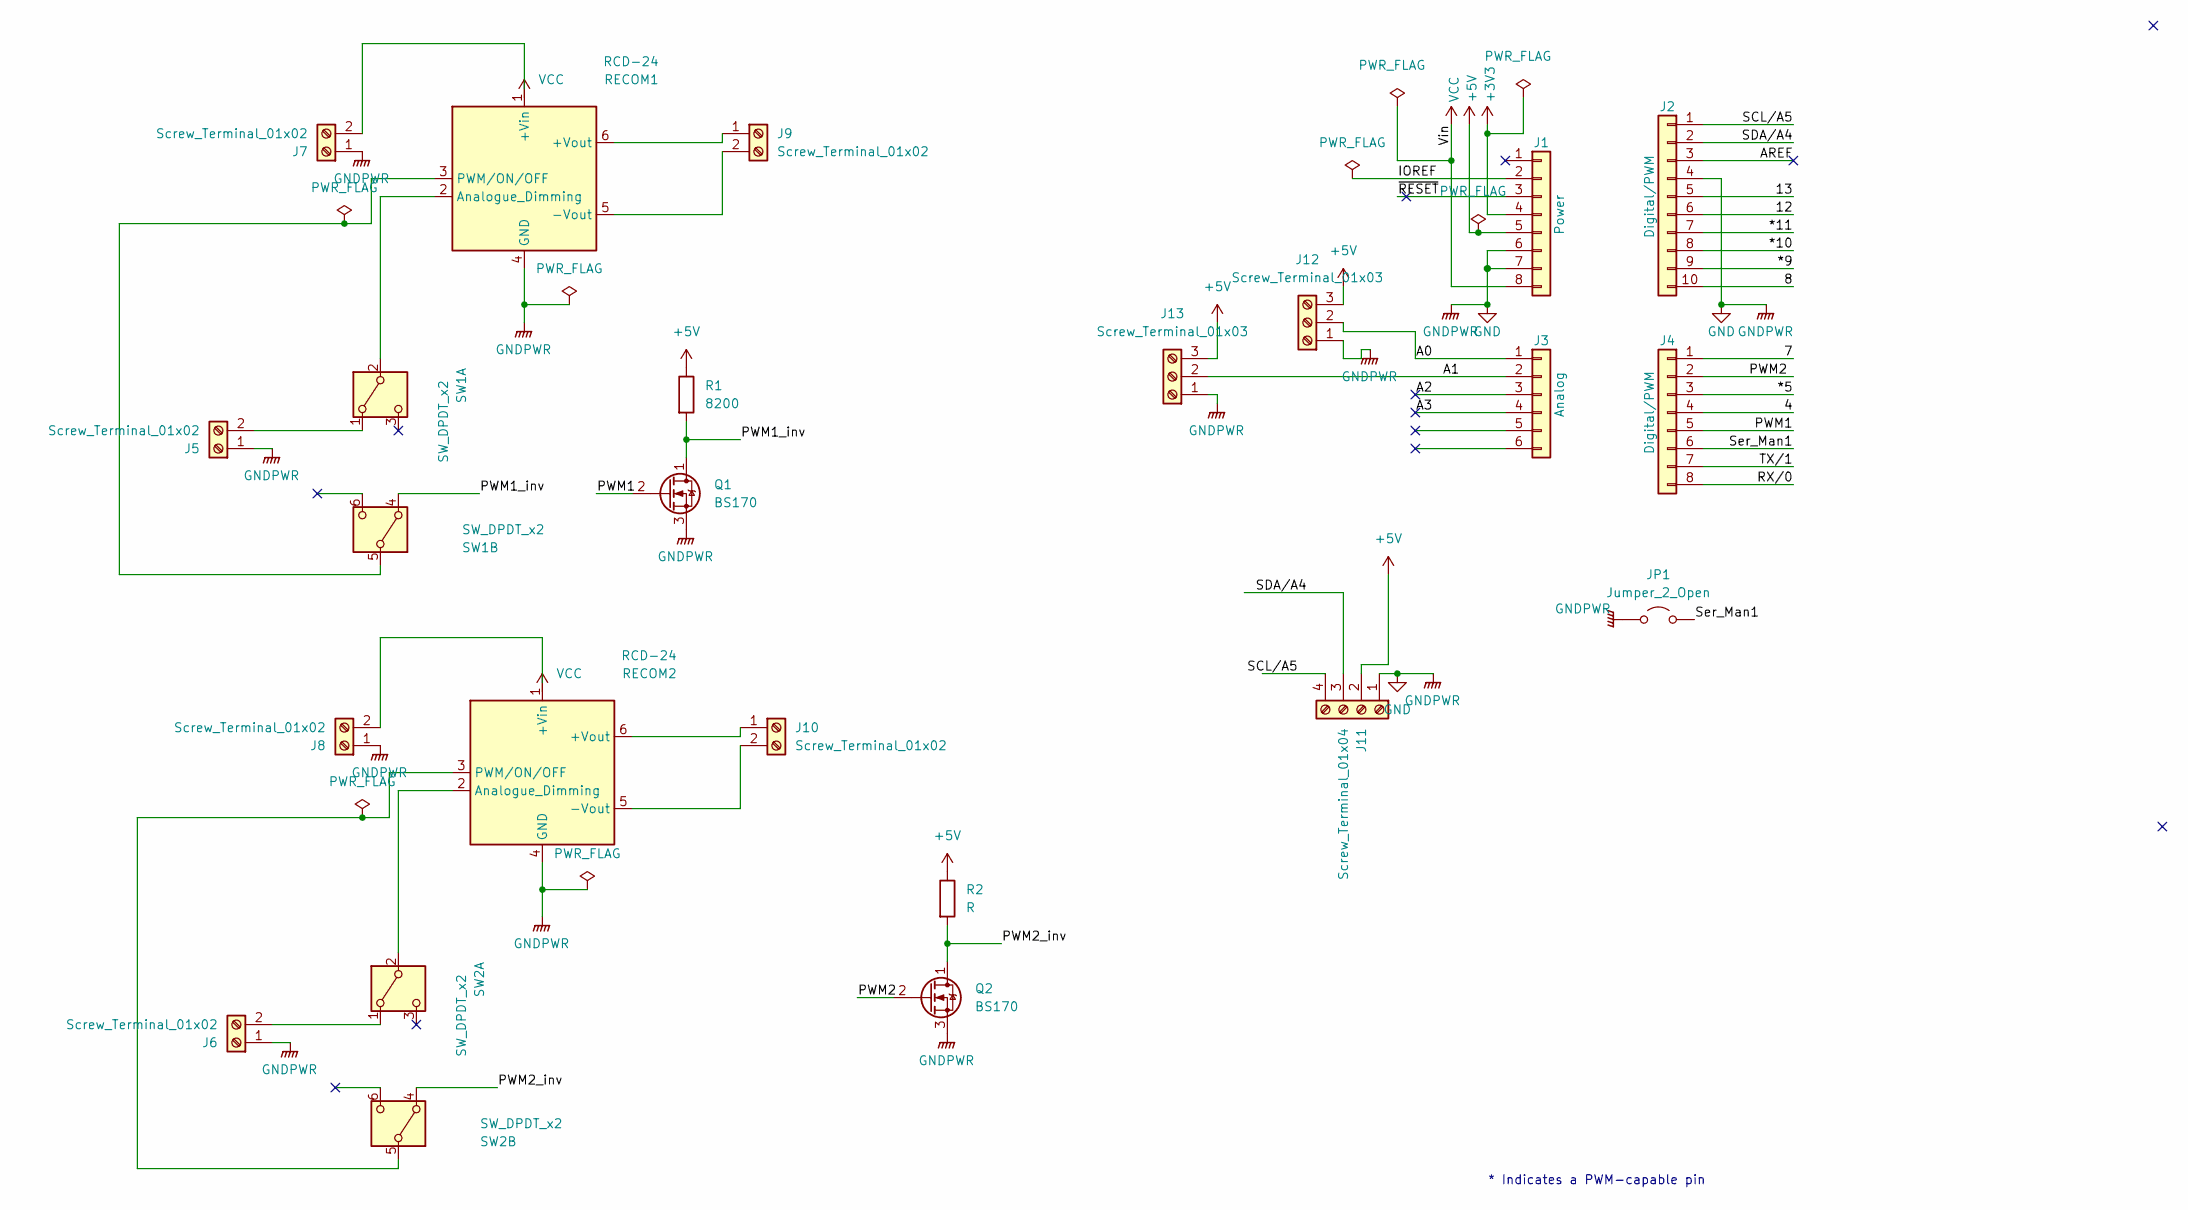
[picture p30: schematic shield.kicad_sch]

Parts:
J1: Power; PinSocket_1x08_P2.54mm_Vertical
J2: Digital/PWM; PinSocket_1x10_P2.54mm_Vertical
J3: Analog; PinSocket_1x06_P2.54mm_Vertical
J4: Digital/PWM; PinSocket_1x08_P2.54mm_Vertical
J5, J6, J7, J8, J9, J10: Screw_Terminal_01x02; PinHeader_2x01_P2.54mm_Vertical
J11: Screw_Terminal_01x04; PinHeader_1x04_P2.54mm_Vertical
J12, J13: Screw_Terminal_01x03; PinHeader_1x03_P2.54mm_Vertical
JP1: Jumper_2_Open; SW_DIP_SPSTx01_Slide_9.78x4.72mm_W7.62mm_P2.54mm_modif
Q1, Q2: BS170; TO-92_Inline
R1: 8200; R_Axial_DIN0207_L6.3mm_D2.5mm_P2.54mm_Vertical
R2: R; R_Axial_DIN0207_L6.3mm_D2.5mm_P2.54mm_Vertical
RECOM1, RECOM2: RCD-24; Converter_DCDC_RECOM_RCD-24_THT
SW1, SW2: SW_DPDT_x2; SW_CK_JS202011CQN_DPDT_Straight

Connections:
+3V3: J1.4
+5V: J1.5, J11.2, J12.3, J13.3, R1.1, R2.1
/4: J4.4
/7: J4.1
/8: J2.10
/12: J2.6
/13: J2.5
/*5: J4.3
/*9: J2.9
/*10: J2.8
/*11: J2.7
/A0: J3.1, J12.2
/A1: J3.2, J13.2
/A2: J3.3
/A3: J3.4
/AREF: J2.3
/IOREF: J1.2
/PWM1: J4.5, Q1.2 (G)
/PWM1_inv: Q1.1 (D), R1.2, SW1.4 (A)
/PWM2: J4.2, Q2.2 (G)
/PWM2_inv: Q2.1 (D), R2.2, SW2.4 (A)
/RX/0: J4.8
/SCL/A5: J2.1, J11.4
/SDA/A4: J2.2, J11.3
/Ser_Man1: J4.6, JP1.2 (B)
/TX/1: J4.7
/~RESET: J1.3
GND: J1.6, J1.7, J2.4, J5.1, J6.1, J7.1, J8.1, J11.1, J12.1, J13.1, JP1.1 (A), Q1.3 (S), Q2.3 (S), RECOM1.4 (GND), RECOM2.4 (GND)
unnamed: J5.2, SW1.1 (A)
unnamed: J6.2, SW2.1 (A)
unnamed: J7.2, RECOM1.1 (+Vin)
unnamed: J8.2, RECOM2.1 (+Vin)
unnamed: J9.1, RECOM1.6 (+Vout)
unnamed: J9.2, RECOM1.5 (-Vout)
unnamed: J10.1, RECOM2.6 (+Vout)
unnamed: J10.2, RECOM2.5 (-Vout)
unnamed: RECOM1.2 (Analogue_Dimming), SW1.2 (B)
unnamed: RECOM1.3 (PWM/ON/OFF), SW1.5 (B)
unnamed: RECOM2.2 (Analogue_Dimming), SW2.2 (B)
unnamed: RECOM2.3 (PWM/ON/OFF), SW2.5 (B)
VCC: J1.8

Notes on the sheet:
* Indicates a PWM-capable pin

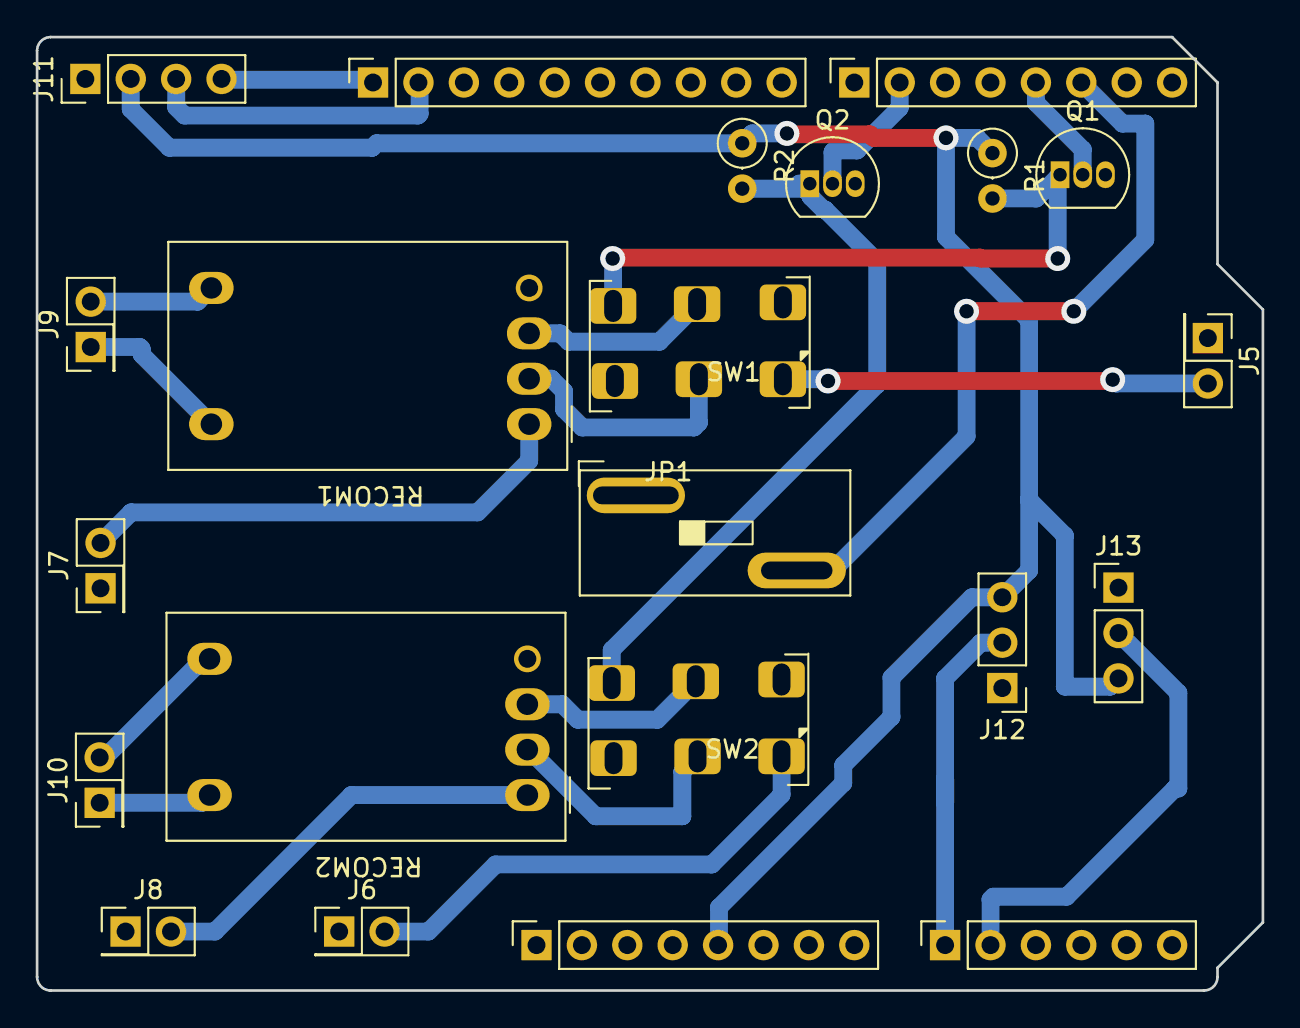
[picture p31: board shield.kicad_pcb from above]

Board: 2 copper layers, 68.6 x 53.3 mm, 23 parts (0 on the bottom side), 23 nets.

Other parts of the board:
MH1: MountingHole_3.2mm

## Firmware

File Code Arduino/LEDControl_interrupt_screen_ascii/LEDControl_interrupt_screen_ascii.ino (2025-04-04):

#include <SSD1306Ascii.h>
#include <SSD1306AsciiAvrI2c.h>
#include <SSD1306AsciiSoftSpi.h>
#include <SSD1306AsciiSpi.h>
#include <SSD1306AsciiWire.h>
#include <SSD1306init.h>

/*
  
  Copyright (C) 2022 Sony Computer Science Laboratories
  
  Author(s) Peter Hanappe, Douglas Boari, Aliénor Lahlou
  
  free software: you can redistribute it and/or modify
  it under the terms of the GNU General Public License as published by
  the Free Software Foundation, either version 3 of the License, or
  (at your option) any later version.
  
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
  You should have received a copy of the GNU General Public License
  along with this program.  If not, see
  <http://www.gnu.org/licenses/>.
  
 */
#include <ArduinoSerial.h>
#include <RomiSerial.h>
#include <RomiSerialErrors.h>
#include <stdint.h>
#include "DigitalPulse.h"
#include "ActivityManager.h"
#include "BoardFactory.h"
#include "ITimer.h"
#include "IBoard.h"
#include "EndSwitch.h"
#include "Relay.h"


#include <Wire.h>
#include "SSD1306Ascii.h"
#include "SSD1306AsciiWire.h"

// 0X3C+SA0 - 0x3C or 0x3D
#define I2C_ADDRESS 0x3C

SSD1306AsciiWire oled;

using namespace romiserial;



void send_info(IRomiSerial *romiSerial, int16_t *args, const char *string_arg);
void handle_add_digital_pulse(IRomiSerial *romiSerial, int16_t *args,
                              const char *string_arg);
void handle_set_secondary(IRomiSerial *romiSerial, int16_t *args, const char *string_arg);
void handle_stop_measurements(IRomiSerial *romiSerial, int16_t *args,
                              const char *string_arg);
void handle_start_mesurements(IRomiSerial *romiSerial, int16_t *args,
                              const char *string_arg);
void handle_add_relay(IRomiSerial *romiSerial, int16_t *args, const char *string_arg);
void handle_is_active(IRomiSerial *romiSerial, int16_t *args, const char *string_arg);
void handle_reset(IRomiSerial *romiSerial, int16_t *args, const char *string_arg);

const static MessageHandler handlers[] = {
        { 'd', 8, false, handle_add_digital_pulse },
        { 'r', 1, false, handle_add_relay },
        { 's', 2, false, handle_set_secondary },
        { 'b', 2, false, handle_start_mesurements },
        { 'e', 0, false, handle_stop_measurements },
        { 'R', 0, false, handle_reset },
        { 'A', 0, false, handle_is_active },
        { '?', 0, false, send_info },
};

static int kMaxActivitiesCode = 1;
static int kBadStartCode = 2;
static int kBadPeriodCode = 3;
static int kBadDurationCode = 4;
static int kBadPinCode = 5;

static char *kMaxActivitiesMessage = "Too many activities";
static char *kBadStartMessage = "Bad start";
static char *kBadPeriodMessage = "Bad period";
static char *kBadDurationMessage = "Bad duration";
static char *kBadPinMessage = "Bad pin";

const byte interruptPin = 2; // switching between manual and serial mode, possible interrupt pin on Uno board: 2 and 3. 
const byte MANUAL = LOW;
const byte USB = HIGH;
byte currentMode = USB; // default mode
int analogPin = A0;  // Potentiometer connected to analog branch A0
int analogPin2 = A1;
int potentio = 255;        // Variable storing the potentiometer value
int potentio2 = 255;
int potentio_prev = 255;        // Variable storing the potentiometer value
int potentio_prev2 = 255;        // Variable storing the potentiometer value


float calc = 0;
int ledPin = 6; // LED pin. PWM pins not interfering with the timer: select among 3, 6, 10 and 11. NOT 5 or 9 !
int ledPin2 = 3; // LED pin. PWM pins not interfering with the timer: select among 3, 6, 10 and 11. NOT 5 or 9 !
volatile byte flag=0; // interrupt switch. Only put volatile variable in the interrupt func, short content, no read/write, no serial. 

#if defined(ARDUINO_SAM_DUE)
ArduinoSerial serial(SerialUSB);
#else
ArduinoSerial serial(Serial);
#endif

RomiSerial romiSerial(serial, serial, handlers, sizeof(handlers) / sizeof(MessageHandler));
ActivityManager activityManager;

IBoard& board = BoardFactory::get();
ITimer& timer = board.get_timer(); // get the board timer

extern volatile int32_t timer_interrupts_;

void set_mode() {
  flag=1;
}



void initial_display_mode(byte currentMode) {
        oled.clear(); //efface affichage écran

        oled.set1X(); //taile normal
        oled.setCursor(0, 0); //positionne curseur en haut à gauche
        oled.println("Mode");
        oled.set2X(); //double la taille
        
        if (currentMode==USB){
          oled.println("SERIAL");
        }
        else if (currentMode==MANUAL) {
          oled.println("MANUAL");
        }
        oled.println(""); //ligne vide
        oled.set1X();
        oled.println("Setting");
        oled.set1X();
        oled.print("1: ");
        oled.print(potentio);
        oled.setCursor(0, 7);
        oled.print("2: ");
        oled.print(potentio2);

        
}

void refresh_mode(byte currentMode) {
        oled.clear(0,128,1,2);
        
        if (currentMode==USB){
          oled.println("SERIAL");
        }
        else if (currentMode==MANUAL) {
          oled.println("MANUAL");
        }

}

int refresh_setting(int potentio, int potentio_prev, int potentio2, int potentio_prev2){
  if (potentio != potentio_prev){
    oled.clear(0,128,6,7);
    oled.print("1: ");
    oled.print(potentio);
    oled.setCursor(0, 7);
    oled.print("2: ");
    oled.print(potentio2);

    return potentio;
  }
  if (potentio2 != potentio_prev2){
    oled.clear(0,128,6,7);
    oled.print("1: ");
    oled.print(potentio);
    oled.setCursor(0, 7);
    oled.print("2: ");
    oled.print(potentio2);

    return potentio2;
  }
  
}


void setup()
{   
    Wire.begin();
    Wire.setClock(400000L);
    oled.begin(&Adafruit128x64, I2C_ADDRESS);
    delay(2000);
    oled.clear();
    oled.setFont(Adafruit5x7);
 
  
#if defined(ARDUINO_SAM_DUE)
        SerialUSB.begin(0);
        while(!SerialUSB);
#else
        Serial.begin(115200);
        while (!Serial)
                ;
#endif
  pinMode(interruptPin, INPUT_PULLUP);
  attachInterrupt(digitalPinToInterrupt(interruptPin), set_mode, CHANGE);
  currentMode = digitalRead(interruptPin); //default mode when no switch is used is Serial (currentMode = USB)
  initial_display_mode(currentMode);
  setupSerial(); // when the code is used separately from the spacific board, it is in serial mode by default (interruptPin HIGH (pullup))
 
}


int read_analog(int pin) //ajout de cette fonction pour éviter les variations
{
    long sum = 0;
    const int numLectures = 10; // Nombre de lectures à moyenner
    for (int i = 0; i < numLectures; i++) 
    {
        sum += analogRead(pin);
        delay(5);  // Petits délais pour éviter de trop ralentir
    }
    return sum / numLectures;
}

void loop()
{
      if (flag == 1) {
        currentMode = digitalRead(interruptPin); // when the switch is switched, a flag is raised to change mode. Mode is indicated by the switch position
      }
      
      if ((flag == 1) && (currentMode==USB)){ // switching from manual to USB
        cleanManual();
        setupSerial();
        refresh_mode(currentMode);
        flag=0;
        }
      else if ((flag == 1) && (currentMode==MANUAL)){ // switching from USB to manual
        cleanSerial();
        setupManual();
        refresh_mode(currentMode);
        flag=0;
        }

      if (currentMode==USB){
        romiSerial.handle_input();
        delay(10);
      }
      else {
      //potentio = analogRead(analogPin);  //read analog value corresponding to potentiometer 
      potentio = read_analog(analogPin); 
      potentio = potentio/4; // adjust the analog range (0-1023) to PWM range (0-255)
      analogWrite(ledPin, potentio);  
      potentio_prev = refresh_setting(potentio, potentio_prev, potentio2, potentio_prev2);

      //potentio2 = analogRead(analogPin2);  //read analog value corresponding to potentiometer
      potentio2 = read_analog(analogPin2);
      potentio2 = potentio2/4; // adjust the analog range (0-1023) to PWM range (0-255)
      analogWrite(ledPin2, potentio2);  
      potentio_prev2 = refresh_setting(potentio, potentio_prev, potentio2, potentio_prev2);

      delay(10);
      }

}

void setupManual(){
    pinMode(ledPin,OUTPUT);
    pinMode(ledPin2,OUTPUT);

}
void cleanManual(){
     analogWrite(ledPin, 0);//j'ai changé ici à 1
     analogWrite(ledPin2, 0);//j'ai changé ici à 1

}

void setupSerial(){
  timer.init();
  timer.start(activityManager.getActivities(),
                    activityManager.countActivities());  
  }


void cleanSerial(){
        analogWrite(ledPin, 0);  //j'ai changé ici à 1
        analogWrite(ledPin2, 0);  //j'ai changé ici à 1

        //IBoard& board = BoardFactory::get();
        //ITimer& timer = board.get_timer();
        timer.stop();
        activityManager.clear();
        delay(10);
  
}


void send_info(IRomiSerial *romiSerial, int16_t *args, const char *string_arg)
{
        romiSerial->send("[\"LightControl\",\"0.1\"]"); 
}

void handle_add_digital_pulse(IRomiSerial *romiSerial, int16_t *args,
                              const char *string_arg)
{
        int8_t pin = (uint8_t) args[0];
        int32_t start_delay = (int32_t) args[1] * 1000 + args[2];
        int32_t duration = (int32_t) args[3] * 1000 + args[4];
        int32_t period = (int32_t) args[5] * 1000 + args[6];
        int value = args[7];
    
        if (start_delay < 0)
                romiSerial->send_error(kBadStartCode, kBadStartMessage);
        else if (period <= 0)
                romiSerial->send_error(kBadPeriodCode, kBadPeriodMessage);
        else if (duration < 0 || duration > period)
                romiSerial->send_error(kBadDurationCode, kBadDurationMessage);
        else if (activityManager.availableSpace() == 0) 
                romiSerial->send_error(kMaxActivitiesCode, kMaxActivitiesMessage);
        else {
                auto activity = new DigitalPulse(pin, start_delay, period,
                                                 duration, value);
                activityManager.addActivity(activity);
                romiSerial->send_ok();
        }
}

void handle_set_secondary(IRomiSerial *romiSerial, int16_t *args, const char *string_arg)
{
        int8_t primary_pin = (uint8_t) args[0];
        int8_t secondary_pin = (uint8_t) args[1];

        IActivity *primary_activity = activityManager.getActivityOnPin(primary_pin);
        IActivity *secondary_activity = activityManager.getActivityOnPin(secondary_pin);

        if (primary_activity == nullptr
            || secondary_activity == nullptr) {
                romiSerial->send_error(kBadPinCode, kBadPinMessage);                
        } else {
                secondary_activity->setPrimary(primary_activity);
                romiSerial->send_ok();
        }
}

void handle_start_mesurements(IRomiSerial *romiSerial, int16_t *args,
                              const char *string_arg)
{
        int32_t duration = (int32_t) args[0] * 1000 + args[1];
        if (duration > 0) {
                auto endSwitch = new EndSwitch(duration);
                activityManager.addActivity(endSwitch);
        }
        
        IBoard& board = BoardFactory::get();
        ITimer& timer = board.get_timer();
        timer.start(activityManager.getActivities(),
                    activityManager.countActivities());
        
        romiSerial->send_ok();
}

void handle_stop_measurements(IRomiSerial *romiSerial, int16_t *args,
                              const char *string_arg)
{
        IBoard& board = BoardFactory::get();
        ITimer& timer = board.get_timer();
        timer.stop();
        
        romiSerial->send_ok();
}

void handle_add_relay(IRomiSerial *romiSerial, int16_t *args, const char *string_arg)
{
        uint8_t pin = args[0];
        auto relay = new Relay(pin);
        activityManager.addActivity(relay);
        romiSerial->send_ok();
}
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

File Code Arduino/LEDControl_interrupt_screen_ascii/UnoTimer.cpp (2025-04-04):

#if defined(ARDUINO_AVR_UNO)

#include <avr/io.h>
#include <avr/interrupt.h>
#include "UnoTimer.h"

#define PRESCALING         1
#define FREQUENCY_STEPPER  25000
#define INTERRUPTS_PER_MILLISECOND 25

volatile uint8_t current_interrupt_ = 0;
volatile int32_t current_time_ms_ = 0;
IActivity **activities_ = 0;
int num_activities_ = 0;
volatile bool running_ = false;

static void clock_init();

static void start_activities();
static void stop_activities();
static inline void update_activities(int32_t ms);

        
UnoTimer::UnoTimer()
{
}

void UnoTimer::init()
{
        cli();
        clock_init();
        sei(); 
}

static void start_timer()
{
        /* Initialize counter */
        TCNT1 = 0;              
        /* Enable Timer1 */     
        TIMSK1 |= (1 << OCIE1A);
}

static void stop_timer()
{
        /* Disable Timer1 interrupt */
        TIMSK1 &= ~(1 << OCIE1A);
}

void UnoTimer::start(IActivity **a, int n)
{
        stop();
        activities_ = a;
        num_activities_ = n;
        start_activities();
        current_interrupt_ = INTERRUPTS_PER_MILLISECOND - 1;
        current_time_ms_ = 0;
        running_ = true;
        start_timer();
}

void UnoTimer::stop()
{
        running_ = false;
        stop_timer();
        stop_activities();
        num_activities_ = 0;
        activities_ = nullptr;
}

bool UnoTimer::isActive()
{
        return running_;
}

// FIXME
static void start_activities()
{
        for (int i = 0; i < num_activities_; i++) {
                activities_[i]->start();
        }
}

// FIXME
static void stop_activities()
{
        for (int i = 0; i < num_activities_; i++) {
                activities_[i]->stop();
        }
}

// FIXME
static inline void update_activities(int32_t ms)
{
        for (int i = 0; i < num_activities_; i++) {
                if (!activities_[i]->isSecondary())
                        activities_[i]->update(ms);
        }
        for (int i = 0; i < num_activities_; i++) {
                if (activities_[i]->isSecondary())
                        activities_[i]->update(ms);
        }
}

static inline void call_activities()
{
        current_interrupt_++;
        if (current_interrupt_ == INTERRUPTS_PER_MILLISECOND) {
                current_interrupt_ = 0;
                if (running_) {
                        update_activities(current_time_ms_);
                }
                current_time_ms_++;
        }
}

/*
 
  https://fr.wikiversity.org/wiki/Micro_contr%C3%B4leurs_AVR/Le_Timer_1
  http://maxembedded.com/2011/07/avr-timers-ctc-mode/
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

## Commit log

2025-03-21 Rename Kicad Complete Circuit.png to Kicad_Complete_Circuit.png
2025-04-04 Mise à jour : ajout et suppression de fichiers dans Images et Solidworks boîte
    [Assemblage1.SLDASM, boîte_pcb.SLDPRT, boîte_pcb.STL, couvercle_pcb.SLDPRT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]
2025-04-04 Mise à jour : ajout dossier kicad
    [shield-B_Cu.gbl, shield-Edge_Cuts.gm1, shield-job.gbrjob, shield.drl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]
2025-06-16 Kicad V2
    [B2B-XH-A.step, B3B-XH-A.step, B4B-XH-A.step, B5B-XH-A.step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]
